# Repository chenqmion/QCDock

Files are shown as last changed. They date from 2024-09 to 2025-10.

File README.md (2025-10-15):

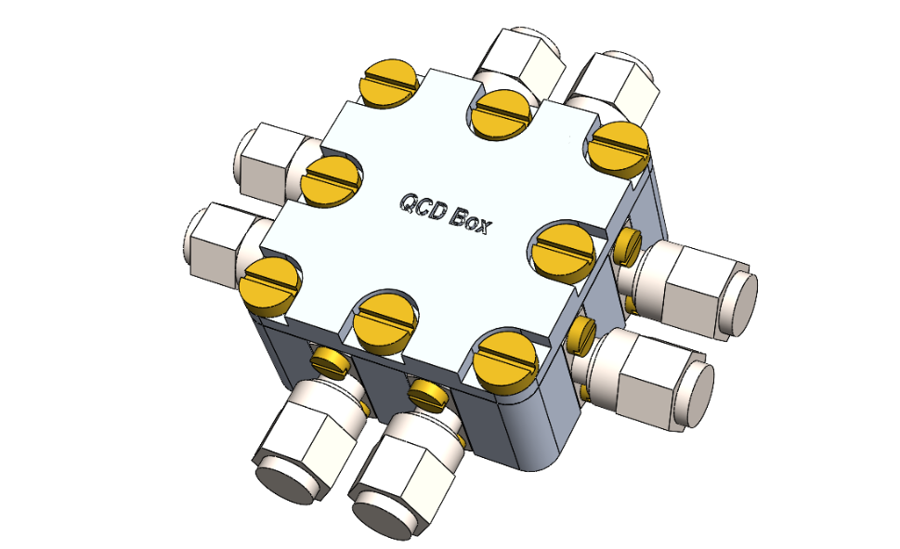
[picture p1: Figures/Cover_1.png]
Preview


# QCDock
This repository contains the **Design** and **Simulation** files of an 8-port sample box developed at QCD Labs. It is designed for 10x10 mm chips. Other chip sizes would require minor modifications of the design files, namely, the PCB and the under-chip cavity. However, chips larger than 13x13mm may encounter wire bonding difficulties.

## Update:
* **20241115** Updated mounting procedure. 
* **20240919** Published V1.0. 

## Description
### Box design in SOLIDWORKS<sup>TM</sup>
* **Box.SLDASM** is the final assembly of the sample box.
* **Bottom.SLDASM** and **Top.SLDASM** are the bottom and top parts, respectively.
* **PCB.SLDASM** is the PCB with GCPW-type transmission lines. <br>
(This file is mainly for consistency check. The actual PCB design files should be found in the **PCB** folder.)
* **SMA.SLDASM** is the SMA connector for consistency check.
* **Chip.SLDASM** is a fake 10x10 mm chip for consistency check.
* **M2_3.SLDASM**, **M2_4.SLDASM**, and **M3_6.SLDASM** are the corresponding screws for consistency check.

\* The **Technical** subfolder contains the .IGS, .SLDDRW, and .pdf files for production.

### PCB design in KiCad<sup>TM</sup>
* **PCB_240916.gds** is the GDSII file designed by a homemade Python<sup>TM</sup> package (pyads).<br>
(pyads is still in the debugging phase and not available to the public at the current time.)
* **gerber** subfolder contains the gerber files.
* The rest of the files are generated by KiCad<sup>TM</sup>.

\* The **.zip** file is for production.

### Box simulation in COMSOL<sup>TM</sup>
* **COMSOL_Eigenmode_Box.mph** simulates the bare box mode.
* **COMSOL_Eigenmode_Full.mph** simulates the box mode with PCB, chip, and wire bonds.<br>
(This file is too large for GitHub. Check out this link to my OneDrive: [COMSOL_Full.mph](https://aaltofi-my.sharepoint.com/:u:/g/personal/qiming_chen_aalto_fi/EXWzsTkU3fFIl8ayYfk28pIBvtJjfRmXe1LOO7rCdNtHGA?e=5WcfCN))

\* The **Geometry** subfolder contains the simplified geometry for simulation.

### PCB simulation in Keysight ADS<sup>TM</sup>
* **QCDBox_wrk.7zads** contains all the simulation files.<br>
(This file is too large for GitHub. Check out this link to my OneDrive: [QCDBox_wrk.7zads](https://aaltofi-my.sharepoint.com/:u:/g/personal/qiming_chen_aalto_fi/EXQFJPZ1qhZAqgtTo-mlQ24B5ay6Y2iGmYVxILdQ2sNBDQ?e=Z6ZQvW))

## Box design 
### Cavity
Bottom (front side)| Bottom (back side)
:---------:|:---------:
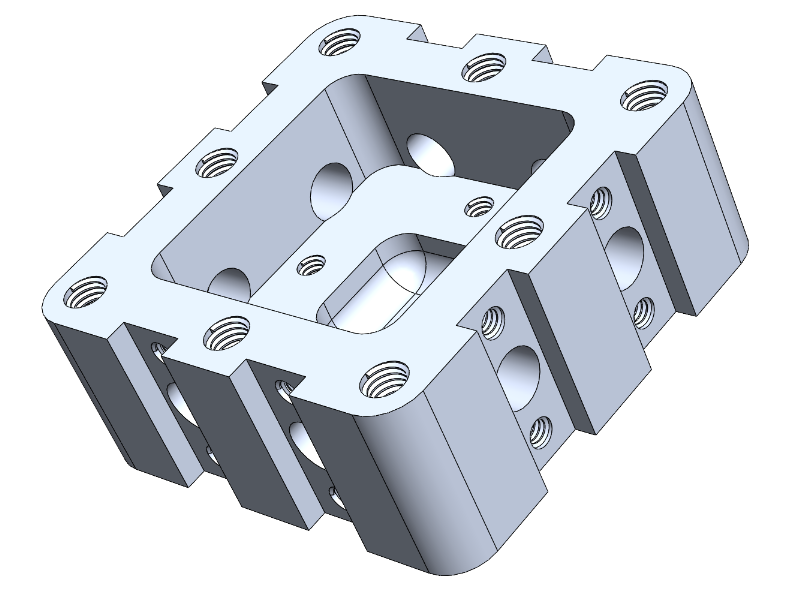
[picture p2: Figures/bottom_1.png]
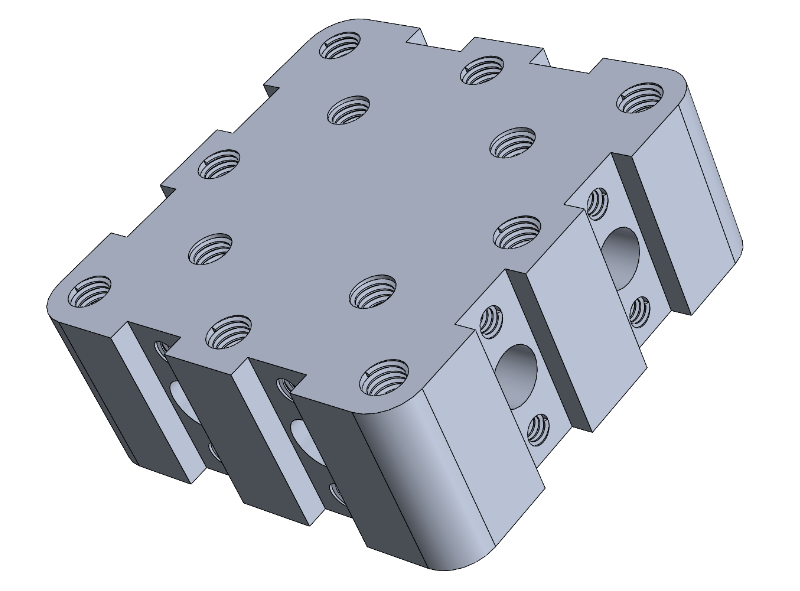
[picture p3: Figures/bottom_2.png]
  |  

Given that the sample box will normally work in the 100MHz -- 8GHz range, we should minimize the box size to push the first box mode as high as possible. The flange size of the SMA connectors (12.9mm) determines the heightness of the box as 13 mm, while its coaxial extention determines the thickness of the side wall as 4 mm. In addition, we add r=3mm fillet for the box.

The inner width of the box is chosen as 21 mm. It will leave a space of 5.5 mm on each side for wire bounding assuming that an 10x10 mm chip is used. This space should be enough considering that the height of the side walls is around 6.5mm. We also add r=2mm fillet for the cavity.

We also designed an empty space below the chip to push the bottom ground further way from the chip. The dimension is 9.5x9.5x3.5 mm in our design, leaving an 0.25 mm distance from the edge to mechanically support the chip. In addition, the chip is supported at the corners by the r=2mm fillet of this under-chip cavity.

Top (front side)| Top (back side)
:---------:|:---------:
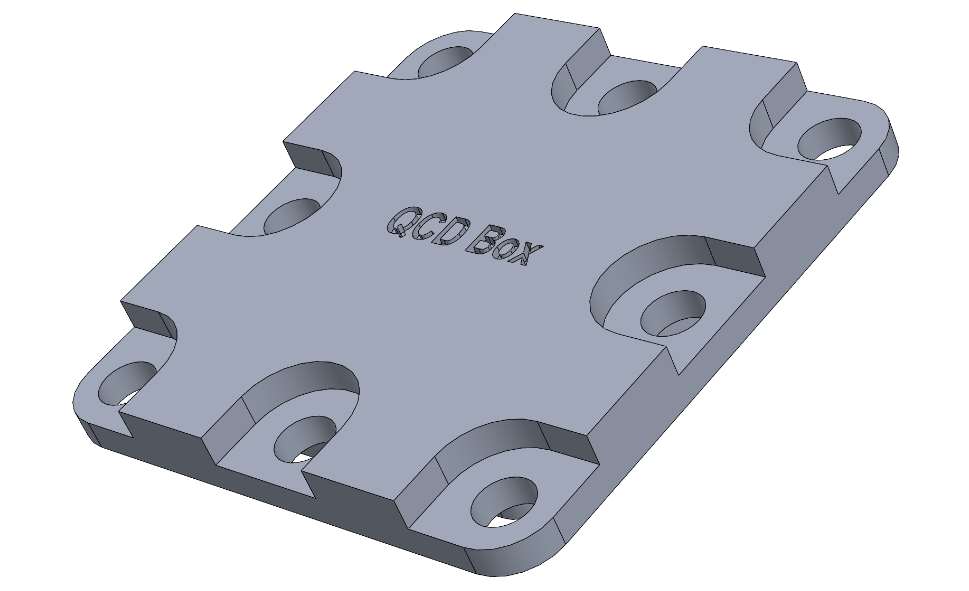
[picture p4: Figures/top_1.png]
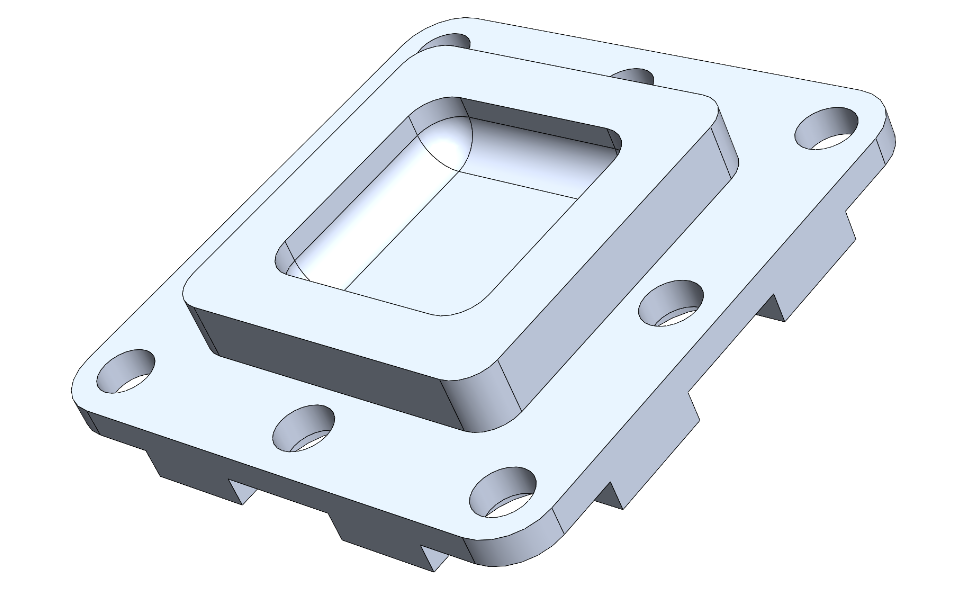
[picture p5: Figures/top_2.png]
  |  

We observe from the simulation that it is useful to have an empty space in the lid to push the first box mode to an even higher frequency. The optimal size of the empty space should be 2/3 of the cavity size, saying 14x14 mm, while the height is not crucial (we choose 3.3 mm). We also add r=2mm fillet for this cavity.

### SMA connectors
To achieve the best impedance match between the SMA connectors and the PCB with minimum efforts, we choose the panel-mount connectors with flat pin. There are only several products of this type available in the market. We choose the M54FM0112F07C model from Micro RF Connector. The extruded pin is 0.8mm-wide and 1.5mm-long, which will determine the launch pad design of the PCB.

The connector has an 0.8mm-diameter 4mm-long impedance-matched extension that can be inserted into the box. They are mounted to the box through 16 M2x4 screws. 

\* The center conductor is gold plated BeCu, which might be slightly magnetic because of Be and the Ni in gold plating process. It may be possible to customize the materials by contacting the company.

### Mounting holes
The box and the lid are assembled with 9 M3x6 screws that are evenly spaced along the edges with an 3mm offset. Owing to the compact size, the threads are designed as through holes that can be used for sample mounting from the back side. 

In addition, we designed 4 addition M3 threads with 3.5mm depth from the back side to faciliate the mounting. A dedicated mounting plate can be used if necessary.

The PCB is mounted inside the cavity via 4 M2x3 screws. Brass may be a good choice of these screws as they provide strength, as well as electrical and thermal condictivities. It will ground the two faces of the PCB to the bulk cavity.

\* Silver paste may be used to improve the electrical and thermal conductivity between the bottom face of PCB and the bulk cavity.

## PCB design 
### GCPW design
We choose ROGERS<sup>TM</sup> 4350B as the PCB material, which has a typical dielectric constant of 3.66. According to ROGERS<sup>TM</sup> online MWI Calculator, the dielectric constant is 3.717 in the "wideband" setting when choosing the thickness as 0.508mm. At specific frequencies, such as 100MHz and 10GHz, it varies from 3.8 to 3.72, respectively. In this design, we choose the dielectric constant at 1GHz as our reference, which is 3.758.

The 0.508mm thickness is chosen for several considerations: The major reason is that a smaller thickness can hardly support the 1mm track width as requested by the SMA connector, assuming that GCPW structure is used. A larger thickness solves this problem, but will lead to a larger geometry that is not very compatible to the chip launcher (a=300um, b=180um). The 0.508mm thickness is a sweet point that fulfils our needs. An additional benefit is that it is comparable to the thickness of our chip (675um).

Impedance (a=1.00 mm, b=0.69 mm)|Impedance 2 (a=0.56 mm, b=0.10 mm)
:---------:|:---------:
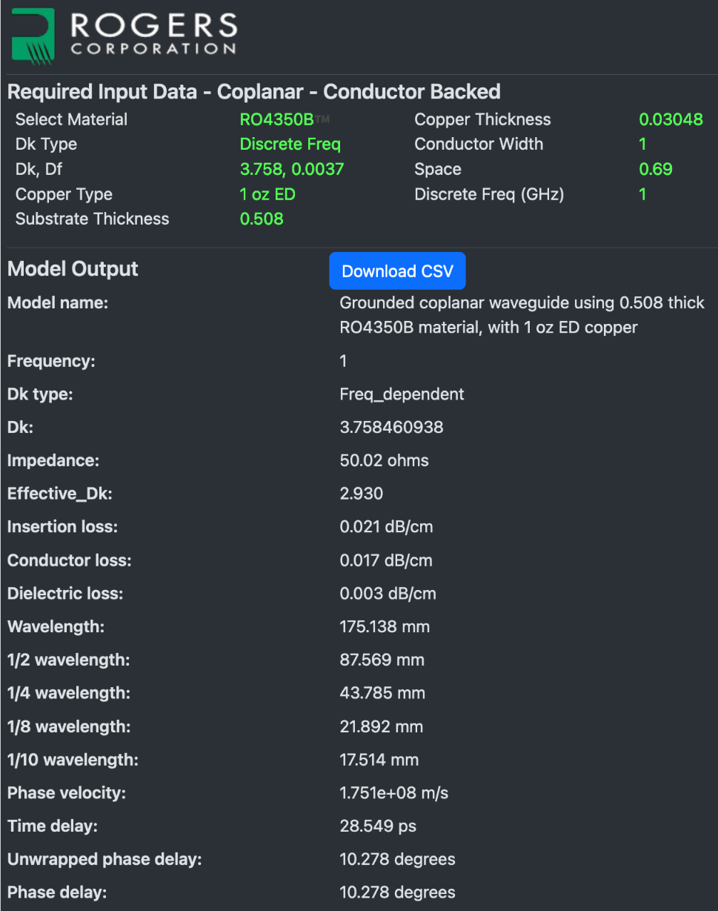
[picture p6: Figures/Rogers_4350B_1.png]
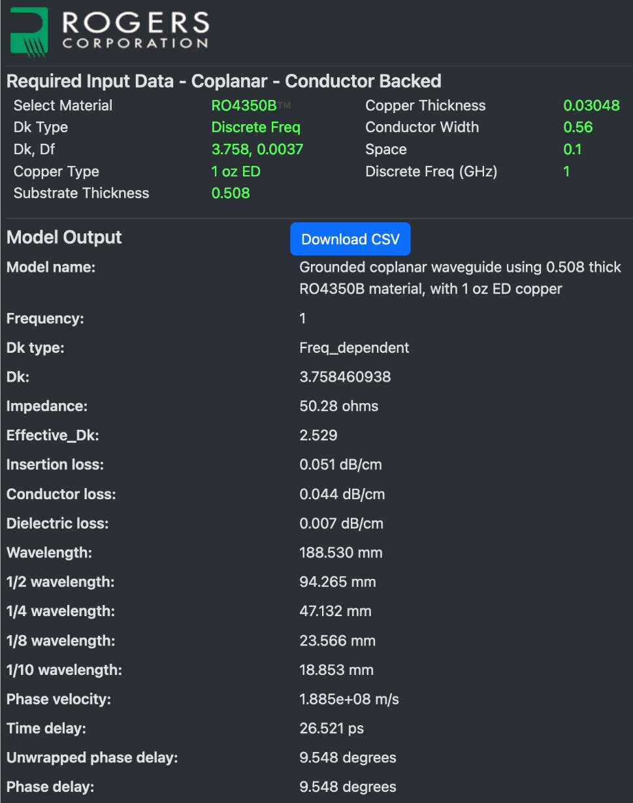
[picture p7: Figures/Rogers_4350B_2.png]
  |  

Using ROGERS<sup>TM</sup> online MWI Calculator, we find two parameter settings that provide good 50Ohm match. Close to the outer side of the PCB, we choose a=1.00mm and b=0.69mm that is convenient for soldering the SMA connectors. We change the design to a=0.56mm and b=0.10mm after 1.5mm from the edge, where an additional 0.65mm taper is designed to connect the two geometries. This 2nd setting is comparable to the on-chip launchers and therefore convenient for wire bonding.

Although a bit skeptical on whether we need vias for such a short waveguide length, the simulation indicates a meaningful improvement of the scattering parameters with them. We choose the via diemeter as 0.2mm. They are 5mm offset from the outer edge of the waveguide slot, and evenly spaced by 8mm alongside the waveguide. In addition, we add vias on the horizontal, vertical, diagonal, and anti-diagonal lines to isolate the 8 waveguides.

PCB (front side)|PCB (back side)
:---------:|:---------:
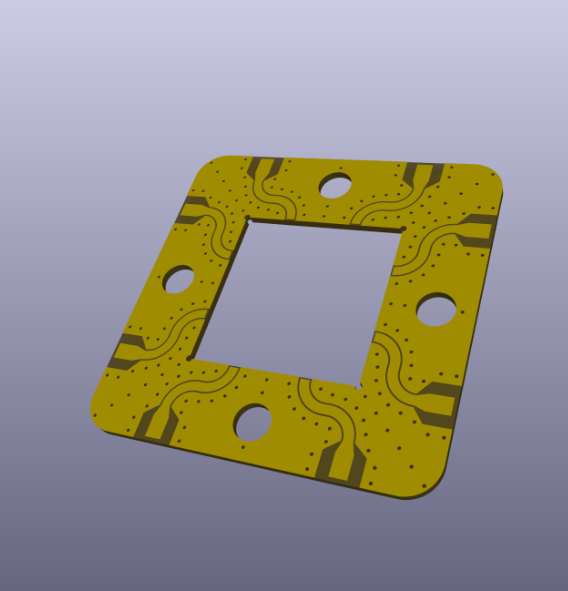
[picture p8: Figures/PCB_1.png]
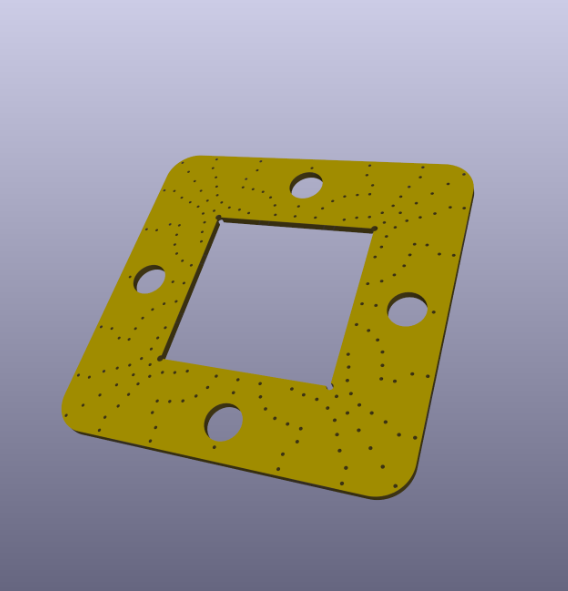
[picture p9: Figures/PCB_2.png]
  |  

The layout is written by a homemade Python<sup>TM</sup> package, pyads. It generates the layout in GDSII format, which can be further converted to gerber files for PCB production (via Keysight ADS<sup>TM</sup>). We find it useful to import the gerber files to KiCad<sup>TM</sup> for a 3D overview. Another benefit is that it can be directly linked to multiple online PCB producers to make the order.

### PCB specification
We choose 2-layer PCB with 1oz copper (35um). The vias are not covered but have 35um-thick copper plating. We choose immersion sliver for surface finish because the standard process of gold plating would require Ni plating beforehand. 

We find in the simulation that the existence of PCB and chip can pull the 1st box mode downwards by multiple gigahertz. This is in some sense unavoidable due to a finite gap between them. However, metalization on the inner edges of the PCB will significantly suppress this effect. We therefore truncate the waveguide 0.1mm from the inner edges and 0.2mm from the outer edges to faciliate edge plating. The 4 screw holes of 2.2mm diameter are also edge plated.

## Box modes
The box-mode simulations are performed by using the Eigenmode solver of COMSOL<sup>TM</sup>. We search for the eigenmodes around 5GHz with normal mesh size. The perfect electric conductor (PEC) condition is applied to the inner surface of the cavity, all the surfaces of PCB, and the upper surface of the chip. In addition, we define 5 wire bonds on each edge of the chip.<br/><br/>

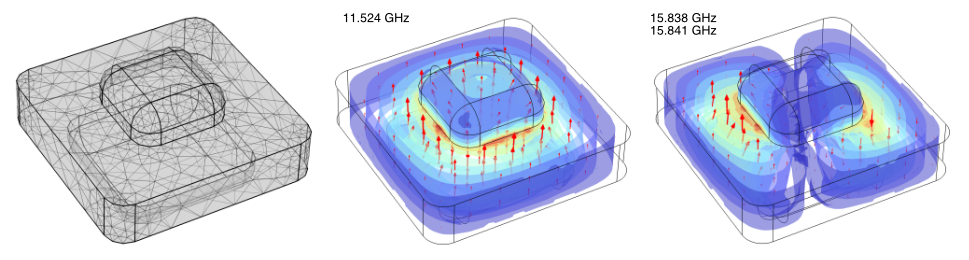
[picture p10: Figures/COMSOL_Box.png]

<em>Fig. 1 Bare box modes. Note that the box is upside down.</em><br/><br/>
We first search for the bare box modes without the PCB and the chip. The first 3 modes are observed at 11.524GHz, 15.838/15.841GHz, and 18.845/18.847GHz, as shown in Fig. 1. This result indicates that the 21mmx21mm cavity size is suitable for operating the box in the 100MHz-8GHz range.<br/><br/>

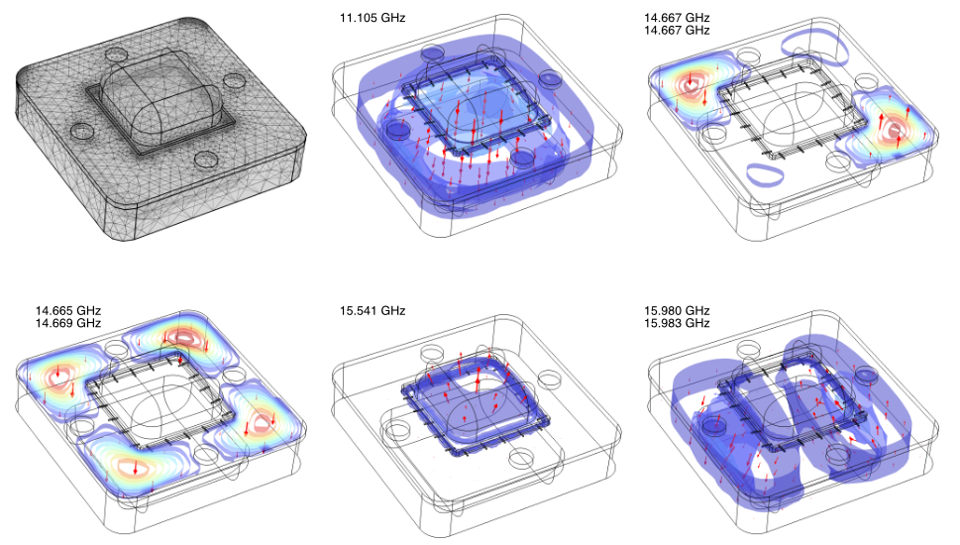
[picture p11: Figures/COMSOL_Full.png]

<em>Fig. 2 Box modes with PCB, chip, and wire bonds. Note that the box is upside down</em><br/><br/>
Next, we add the PCB, chip, and the wire bonds for simulation. The results are summarized in Fig. 2. We find that the 1st are box mode is pulled down to 11.303GHz by introducing the PCB and the chip. The next 4 modes are observed at 11.910/11.912GHz, 14.551GHz, 14.665/14.667/14.669GHz, and 16.226/16.228GHz. Here, the first 2 modes are mostly concentrated to the PCB, the 3rd one is approximately the under-chip cavity mode, while the last one is reminiscent to the 2nd bare box mode.<br/><br/>

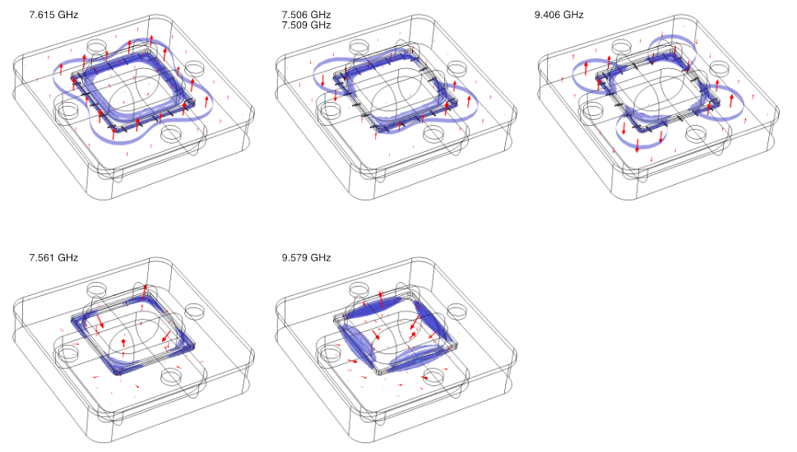
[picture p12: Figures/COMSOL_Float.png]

<em>Fig. 3 Box modes with a floating chip. The upper row has widebonds but not edge plating, while the lower row has edge plating but not wire bonds. Note that the box is upside down</em><br/><br/>
We mentioned before that edge plating of the PCB is important to prevent a substential drop of the 1st box mode in the full simulation. Figure 3 shows the cases with only wire bonds and only edge plating. In both cases, the 1st box mode drops significantly to approximately 7.5GHz. However, the field profiles suggest different mechanisms for the drop: The mode spreads over the PCB in the former case, while it is mostly concentrated in the gap between PCB and the chip in the latter case. This observation reveals the importance of PCB edge plating. Fortunately, it is a standard technique in the PCB inductry.

## PCB characteristics
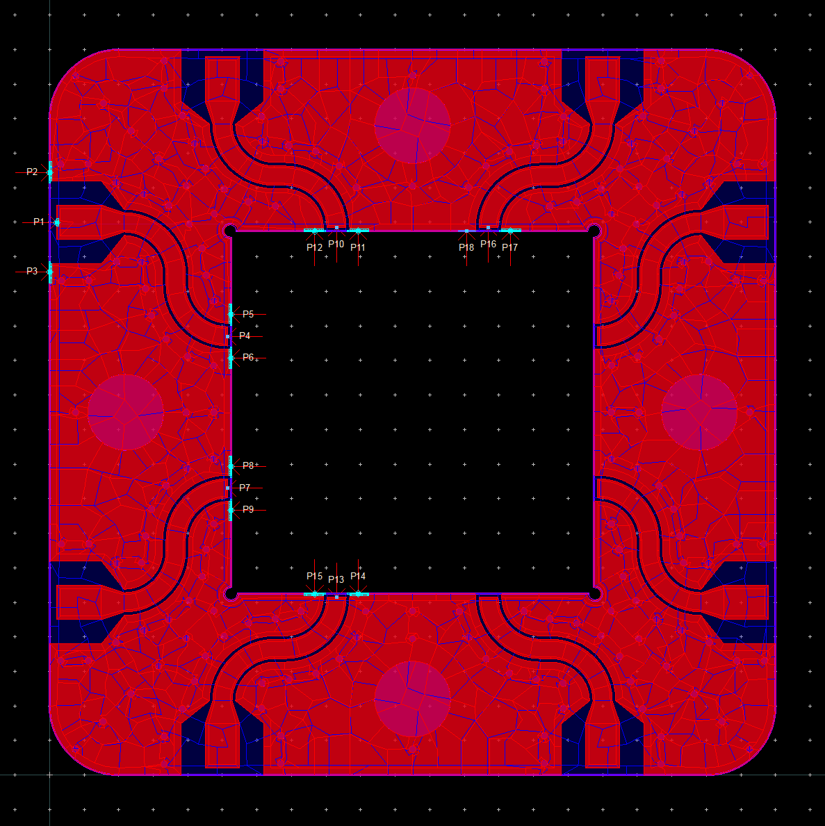
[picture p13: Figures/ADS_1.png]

<em>Fig. 4 Mesh and port definition for PCB simulation.</em><br/><br/>
The PCB simulations are performed by using the Momentum solver of Keysight ADS<sup>TM</sup>. We define the WN port as the inout port, while the rest as output ports. The pin edge size connected to the center conductor is 0.1mm, while it is 0.5mm when connected to the top-face ground.

We simulate the scattering coefficients of the WN waveguide, as well as its crosstalk to the nearest and next nearest waveguides. We perform the adaptive frequency sweep from DC to 10GHz with maximamly 51 points. The mesh is defined at the highest simulation frequency with a density of 20 per wavelength. The automatic edge mesh is enabled and mesh reduction allowed.

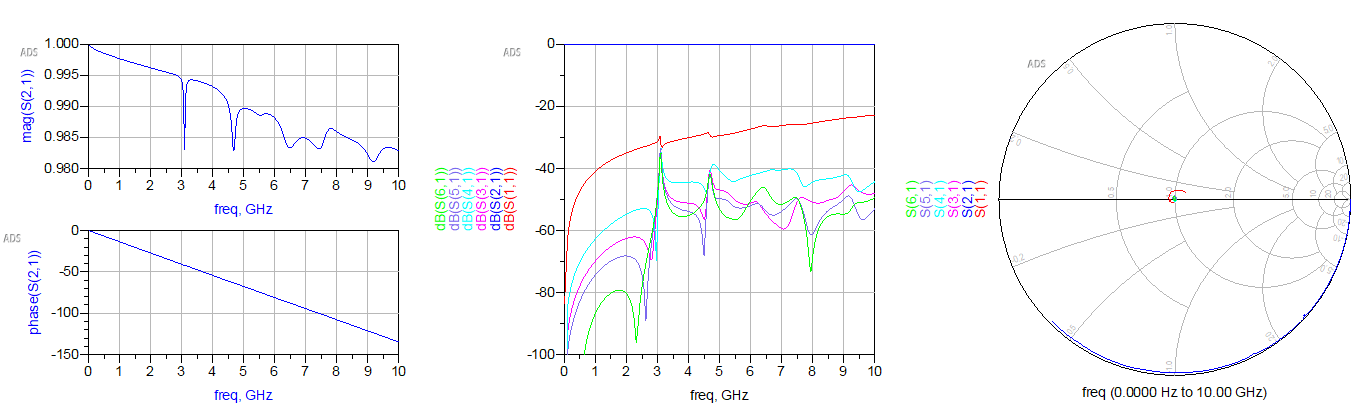
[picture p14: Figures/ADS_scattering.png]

<em>Fig. 5 Scattering parameters.</em><br/><br/>
Figure 5 summarizes the simulation results. The transmission and reflection rates of a single waveguide are -0.18dB and -22dB in the worst case, respectively. It indicates a good 50OHm impedance match, as can be also seen from the Smith chart. Moreover, the crosstalk between nearest and next nearest waveguides are approximately -50dB.<br/><br/>

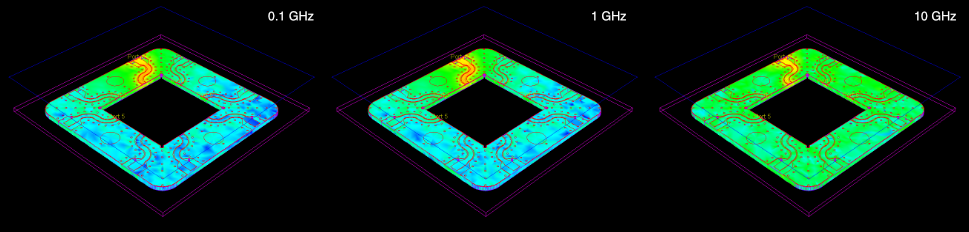
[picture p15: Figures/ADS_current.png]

<em>Fig. 6 Current density in dB scale.</em><br/><br/>
We observe impedance mismatches at 3, 4.7, 6.5GHz in the scattering coefficients. However, the current density profile does not show obvious difference at these frequencies. We note that this mismatch perturbes the transmission rate by less than 1%, although it may look huge in the dB scale. 

## Mounting procedure:
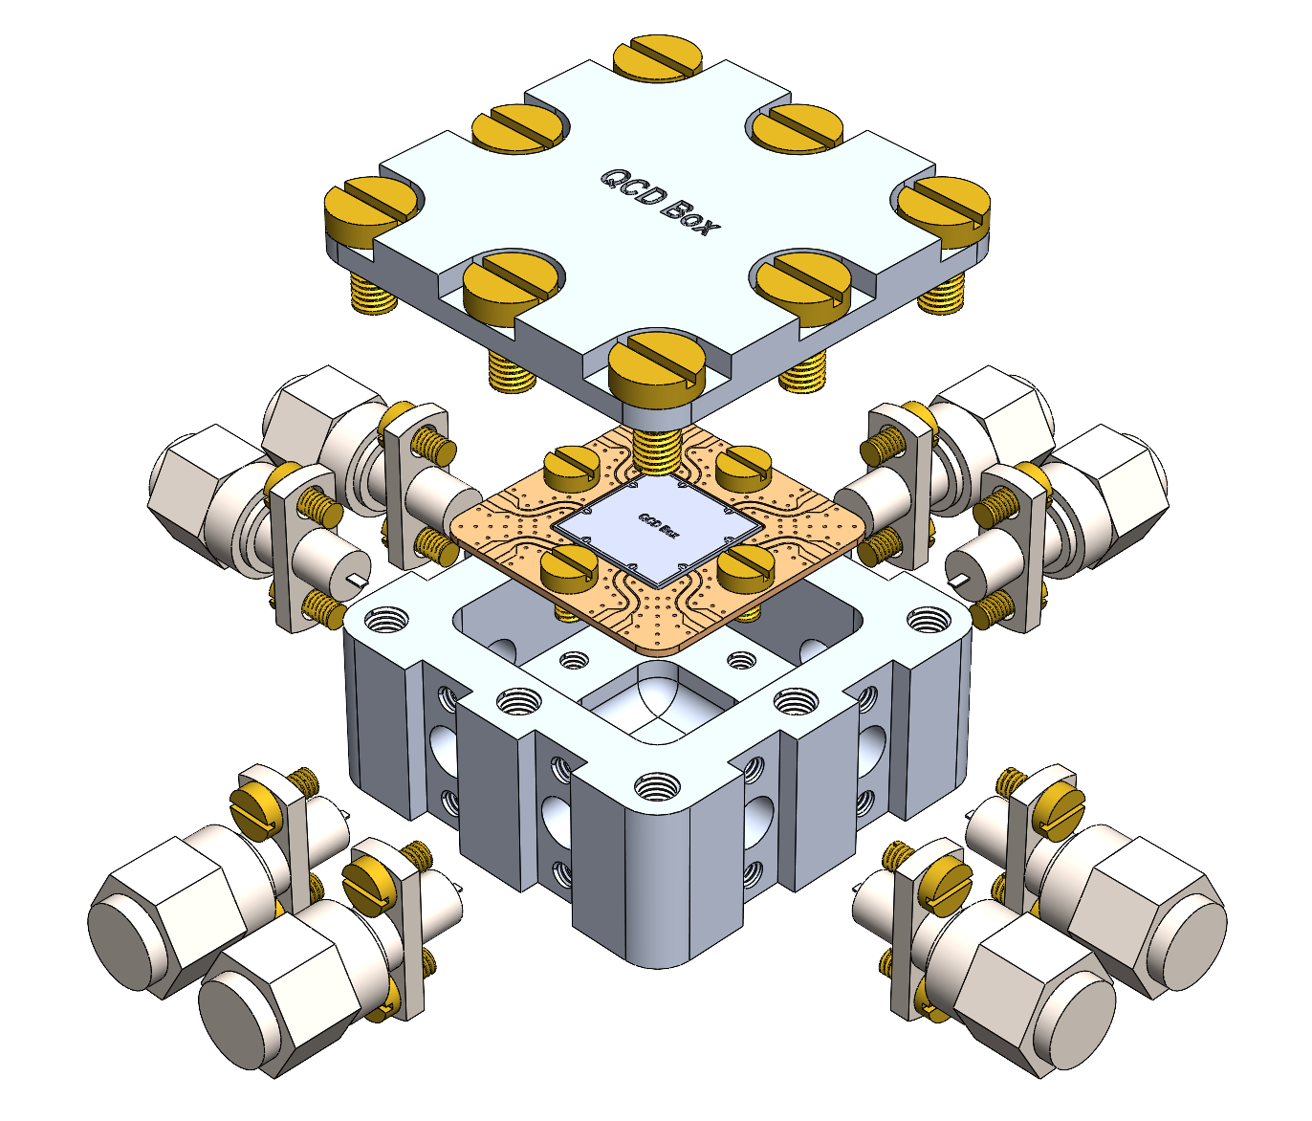
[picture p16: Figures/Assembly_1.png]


Place PCB inside the cavity, align it to the center, and mount it with the 4 M2x3 screws (This will prevent pulling up the PCB during soldering, which is originated from the surface tension of the solder when melting).

Spread a very small amount of solder paste onto the waveguide tracks, then onto the tips of SMA connectors.

Insert the SMA connectors into the holes on the side wall and tighten them with M2x4 screws. 

Check if the solder paste have a good contact between the SMA tip and the waveguide track. Use needle to add more solder paste if necessary.

Use heat gun to melt the solder paste (Use its highest power). The solder paste starts floating in ~30s, and start turning into a shining color in ~1min. 

Wait for ~10s more so that all the soldering areas looks shining and smooth. 

Turn off the heat gun and use twizer to transfer the box into a cold metal plate (The box is very hot right now).

Wait ~5min for cool down, then use multimeter to check DC connection between the SMA pin and the waveguide.

## Acknowledgement:
We are delighted if you find this project helpful to your own study. Feel free to contact us if you have questions, suggestions, criticisms, etc. You are free to copy, share, and build on this project without notifying the authors.

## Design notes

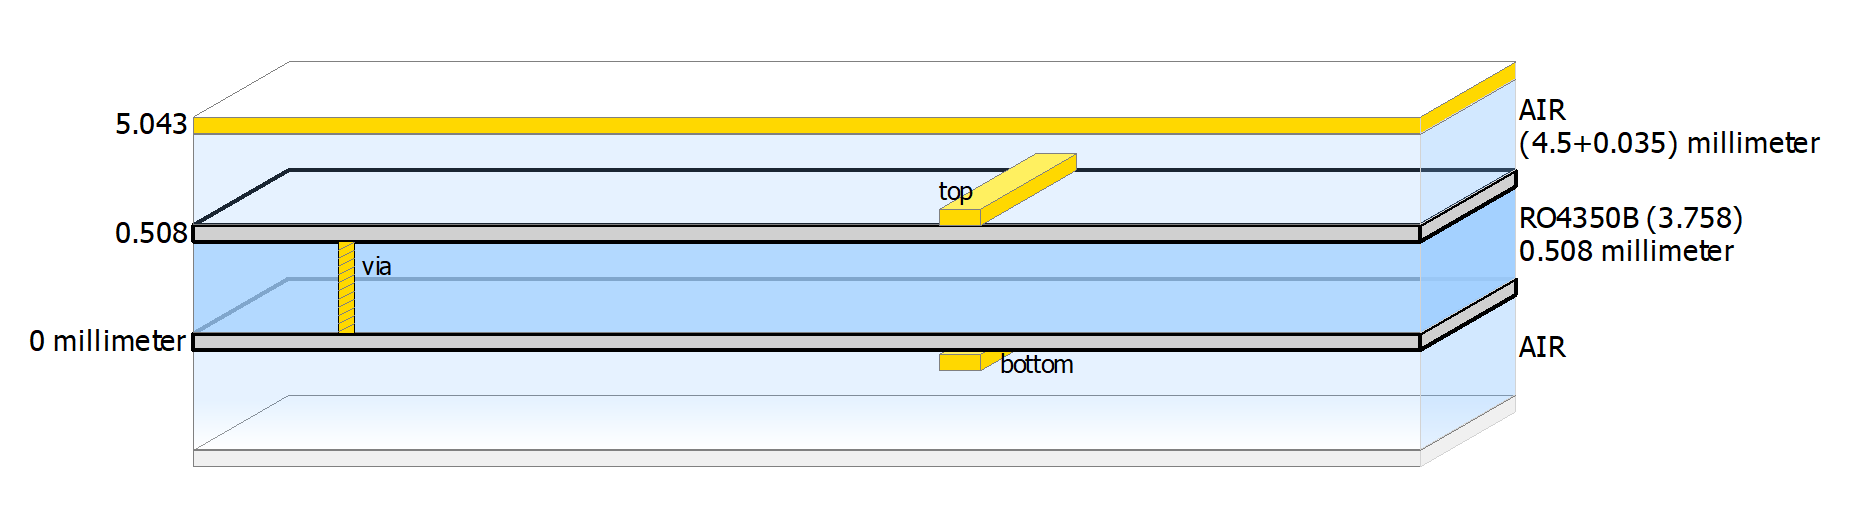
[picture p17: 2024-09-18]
Figures/ADS_2.png

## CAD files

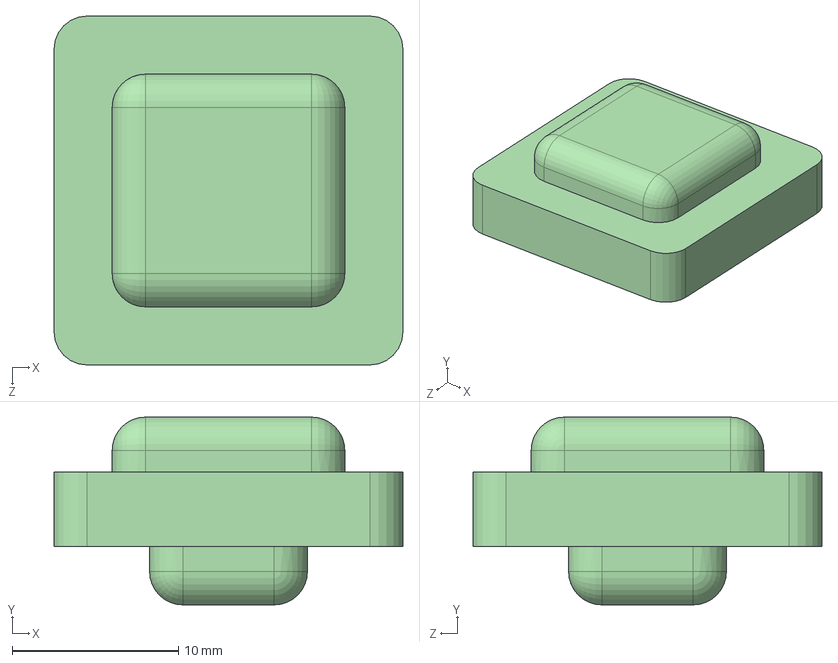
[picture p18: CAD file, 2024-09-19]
COMSOL/Geometry/COMSOL_QCDBox.SLDASM
21.0 x 11.3 x 21.0 mm
COMSOL_Box
COMSOL_PCB
COMSOL_Chip
COMSOL_Bond x 2

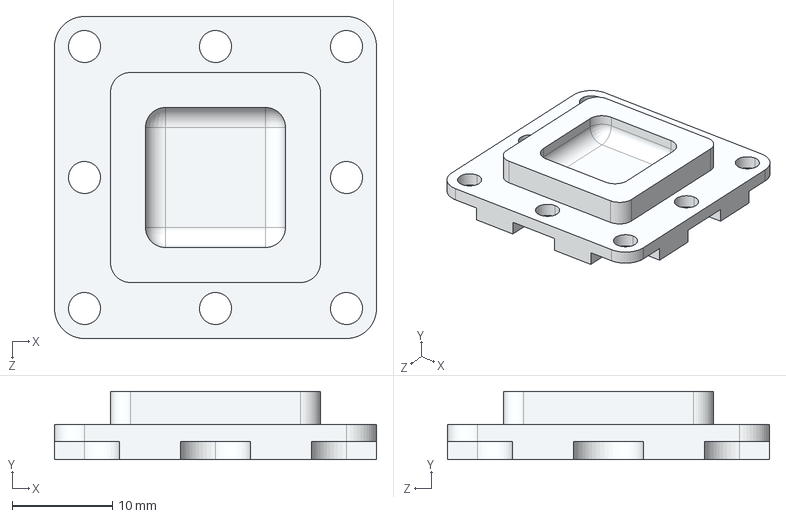
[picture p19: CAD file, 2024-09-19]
Box/Technical/top.IGS
32.2 x 6.80 x 32.2 mm

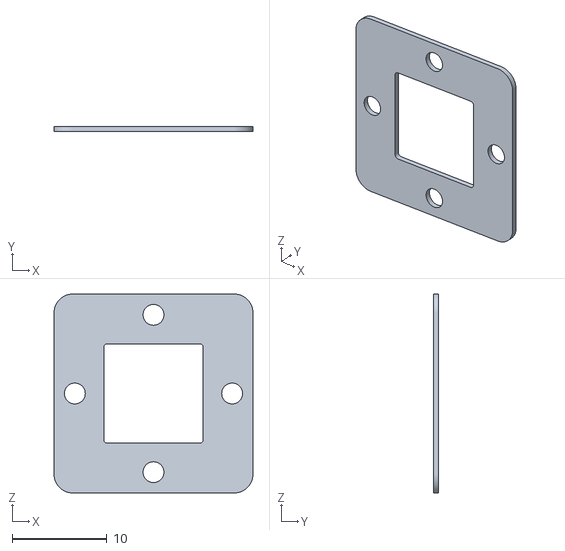
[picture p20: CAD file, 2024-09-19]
COMSOL/Geometry/COMSOL_QCDBox - COMSOL_PCB-1.STL
21.0 x 0.58 x 21.0

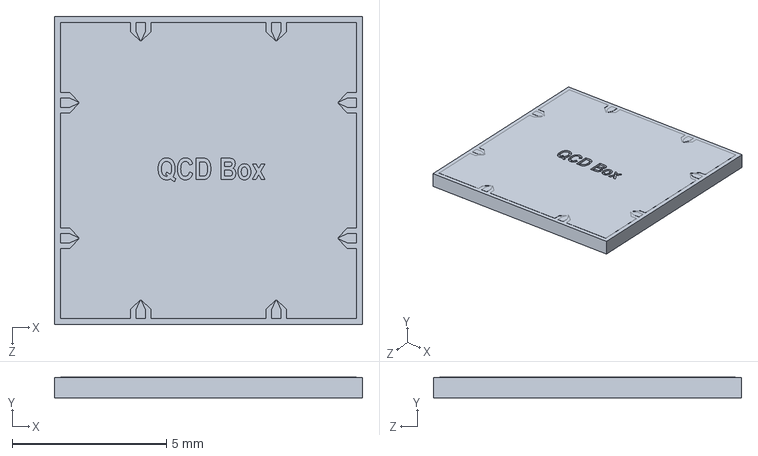
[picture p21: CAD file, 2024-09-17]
Box/chip.SLDPRT
10.0 x 0.675 x 10.0 mm

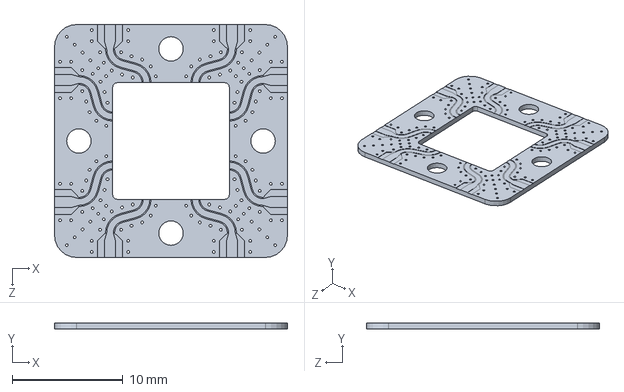
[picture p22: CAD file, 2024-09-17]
Box/PCB.SLDPRT
21.0 x 0.58 x 21.0 mm

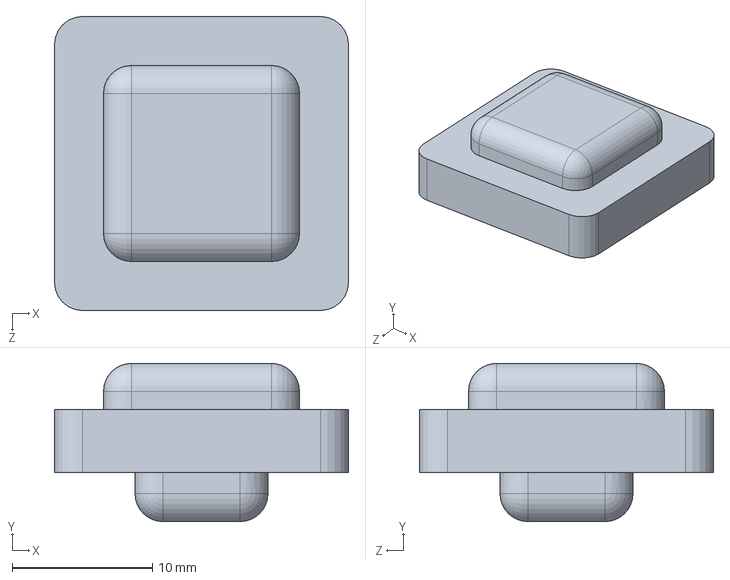
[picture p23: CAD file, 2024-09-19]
COMSOL/Geometry/COMSOL_Box.SLDPRT
21.0 x 11.3 x 21.0 mm

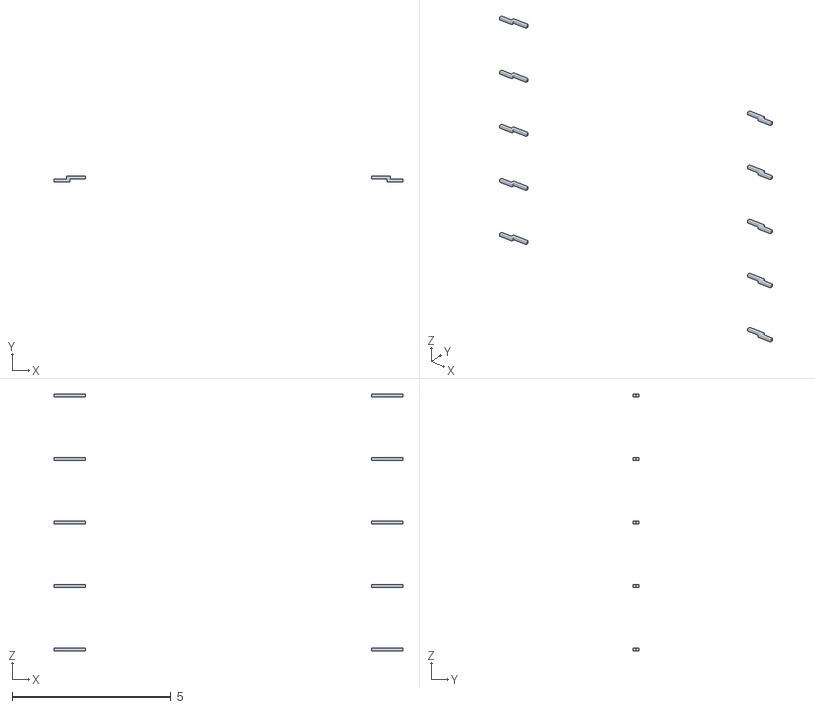
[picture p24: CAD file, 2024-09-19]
COMSOL/Geometry/COMSOL_QCDBox - COMSOL_Bond-1.STL
11.0 x 0.2 x 8.10

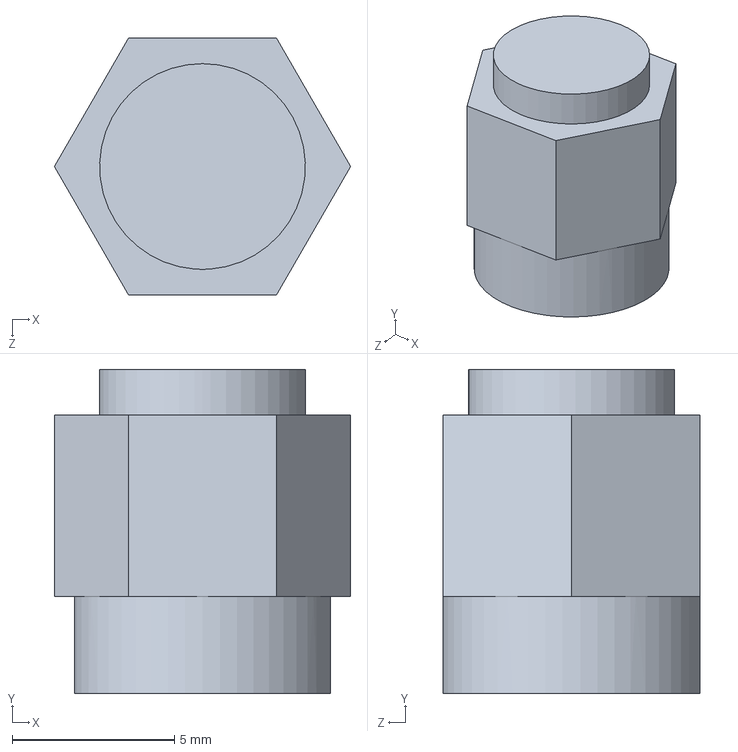
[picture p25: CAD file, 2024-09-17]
Box/SMA_short.SLDPRT
9.15 x 10.0 x 7.92 mm

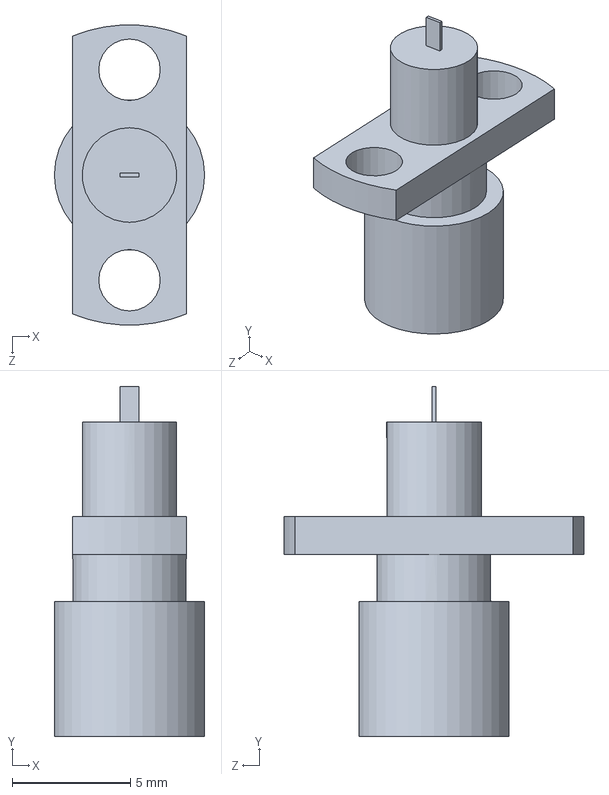
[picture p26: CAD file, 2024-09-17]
Box/SMA.SLDPRT
6.35 x 14.8 x 12.7 mm

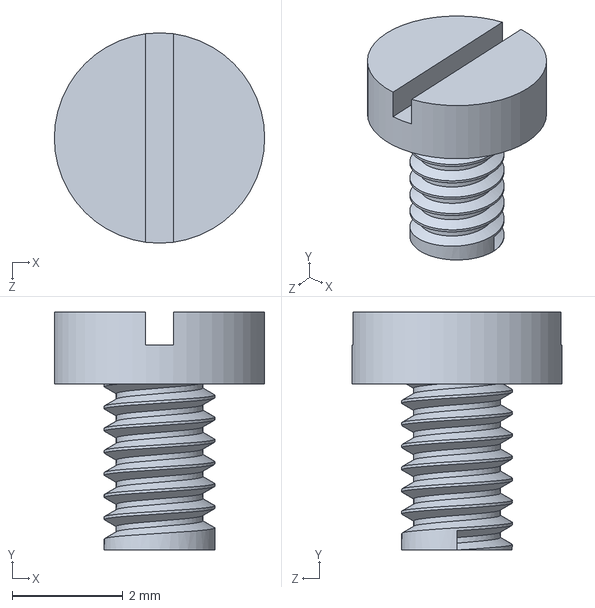
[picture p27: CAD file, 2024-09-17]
Box/M2_3mm.SLDPRT
3.80 x 4.30 x 3.80 mm

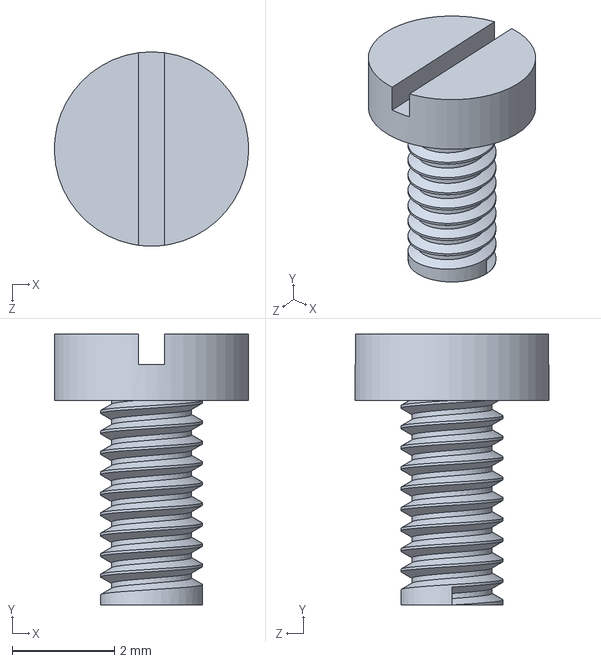
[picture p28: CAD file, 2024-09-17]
Box/M2_4mm.SLDPRT
3.80 x 5.30 x 3.80 mm

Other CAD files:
COMSOL/Geometry/COMSOL_QCDBox - COMSOL_Chip-1.STL
COMSOL/Geometry/COMSOL_QCDBox - COMSOL_Bond-2.STL
Box/top.SLDPRT
COMSOL/Geometry/COMSOL_QCDBox - COMSOL_Box-1.STL
COMSOL/Geometry/COMSOL_PCB.SLDPRT
COMSOL/Geometry/COMSOL_Chip.SLDPRT
COMSOL/Geometry/COMSOL_Bond.SLDPRT
Box/M3_6mm.SLDPRT
Box/Technical/top.SLDDRW

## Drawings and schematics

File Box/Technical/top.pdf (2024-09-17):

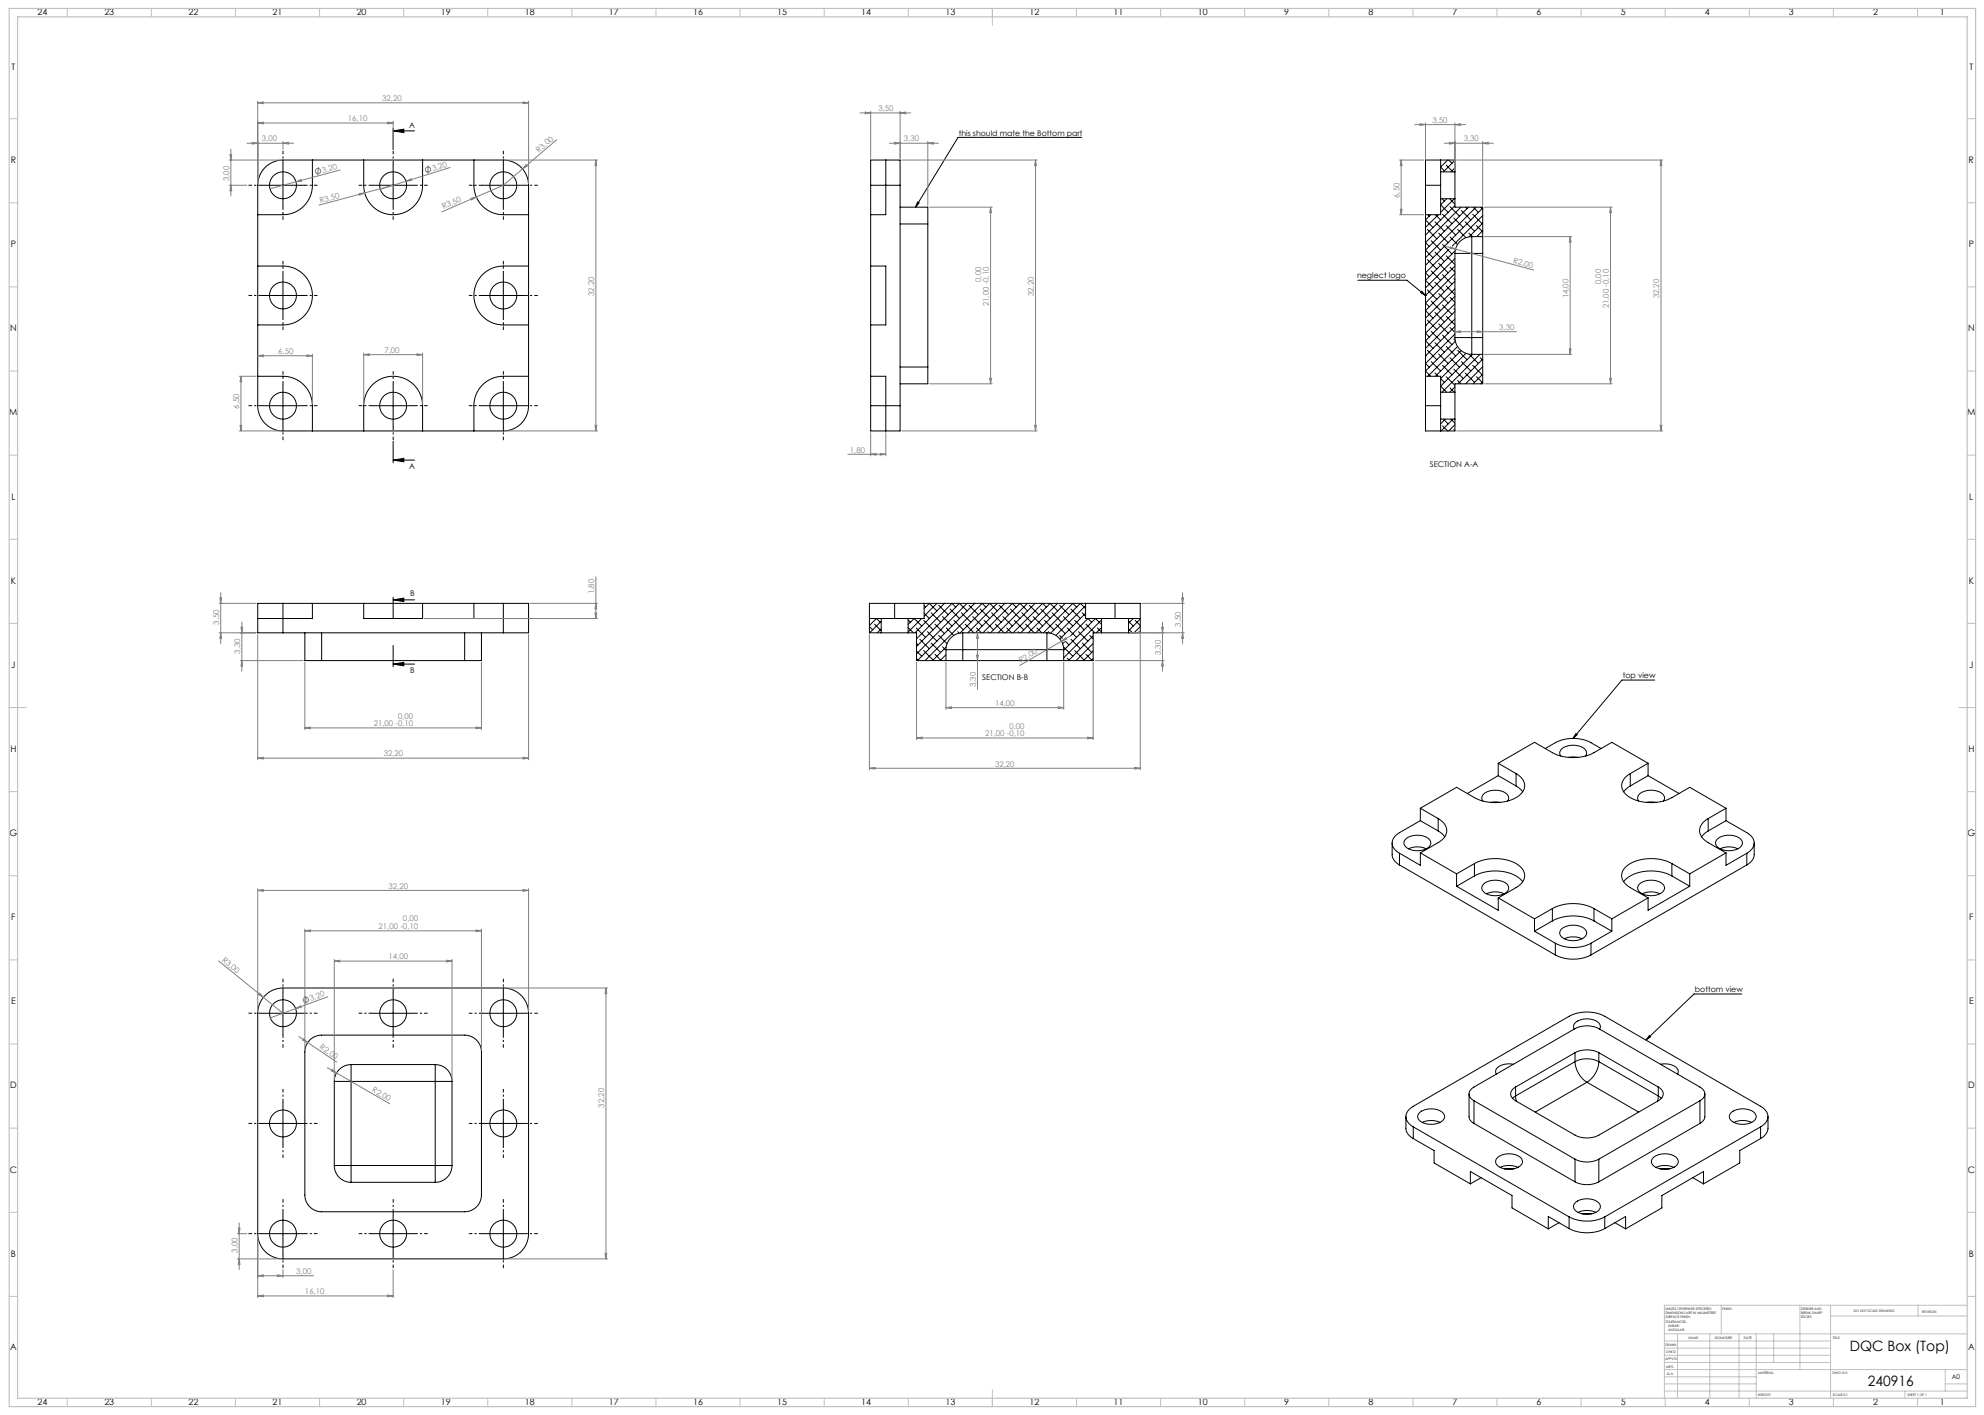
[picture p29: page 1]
top view; bottom view; SECTION A-A; neglect logo; SECTION B-B; FINISH:; DEBURR AND; BREAK SHARP; DO NOT SCALE DRAWING; REVISION; SCALE:5:1; SHEET 1 OF 1; DQC Box (Top)

this should mate the Bottom part

UNLESS OTHERWISE SPECIFIED:
DIMENSIONS ARE IN MILLIMETERS
SURFACE FINISH:
TOLERANCES:
LINEAR:
ANGULAR:

NAME | SIGNATURE | DATE | | | | TITLE:

DRAWN
CHK'D
APPV'D
MFG
Q.A | | | | MATERIAL: | DWG NO. 240916 | A0

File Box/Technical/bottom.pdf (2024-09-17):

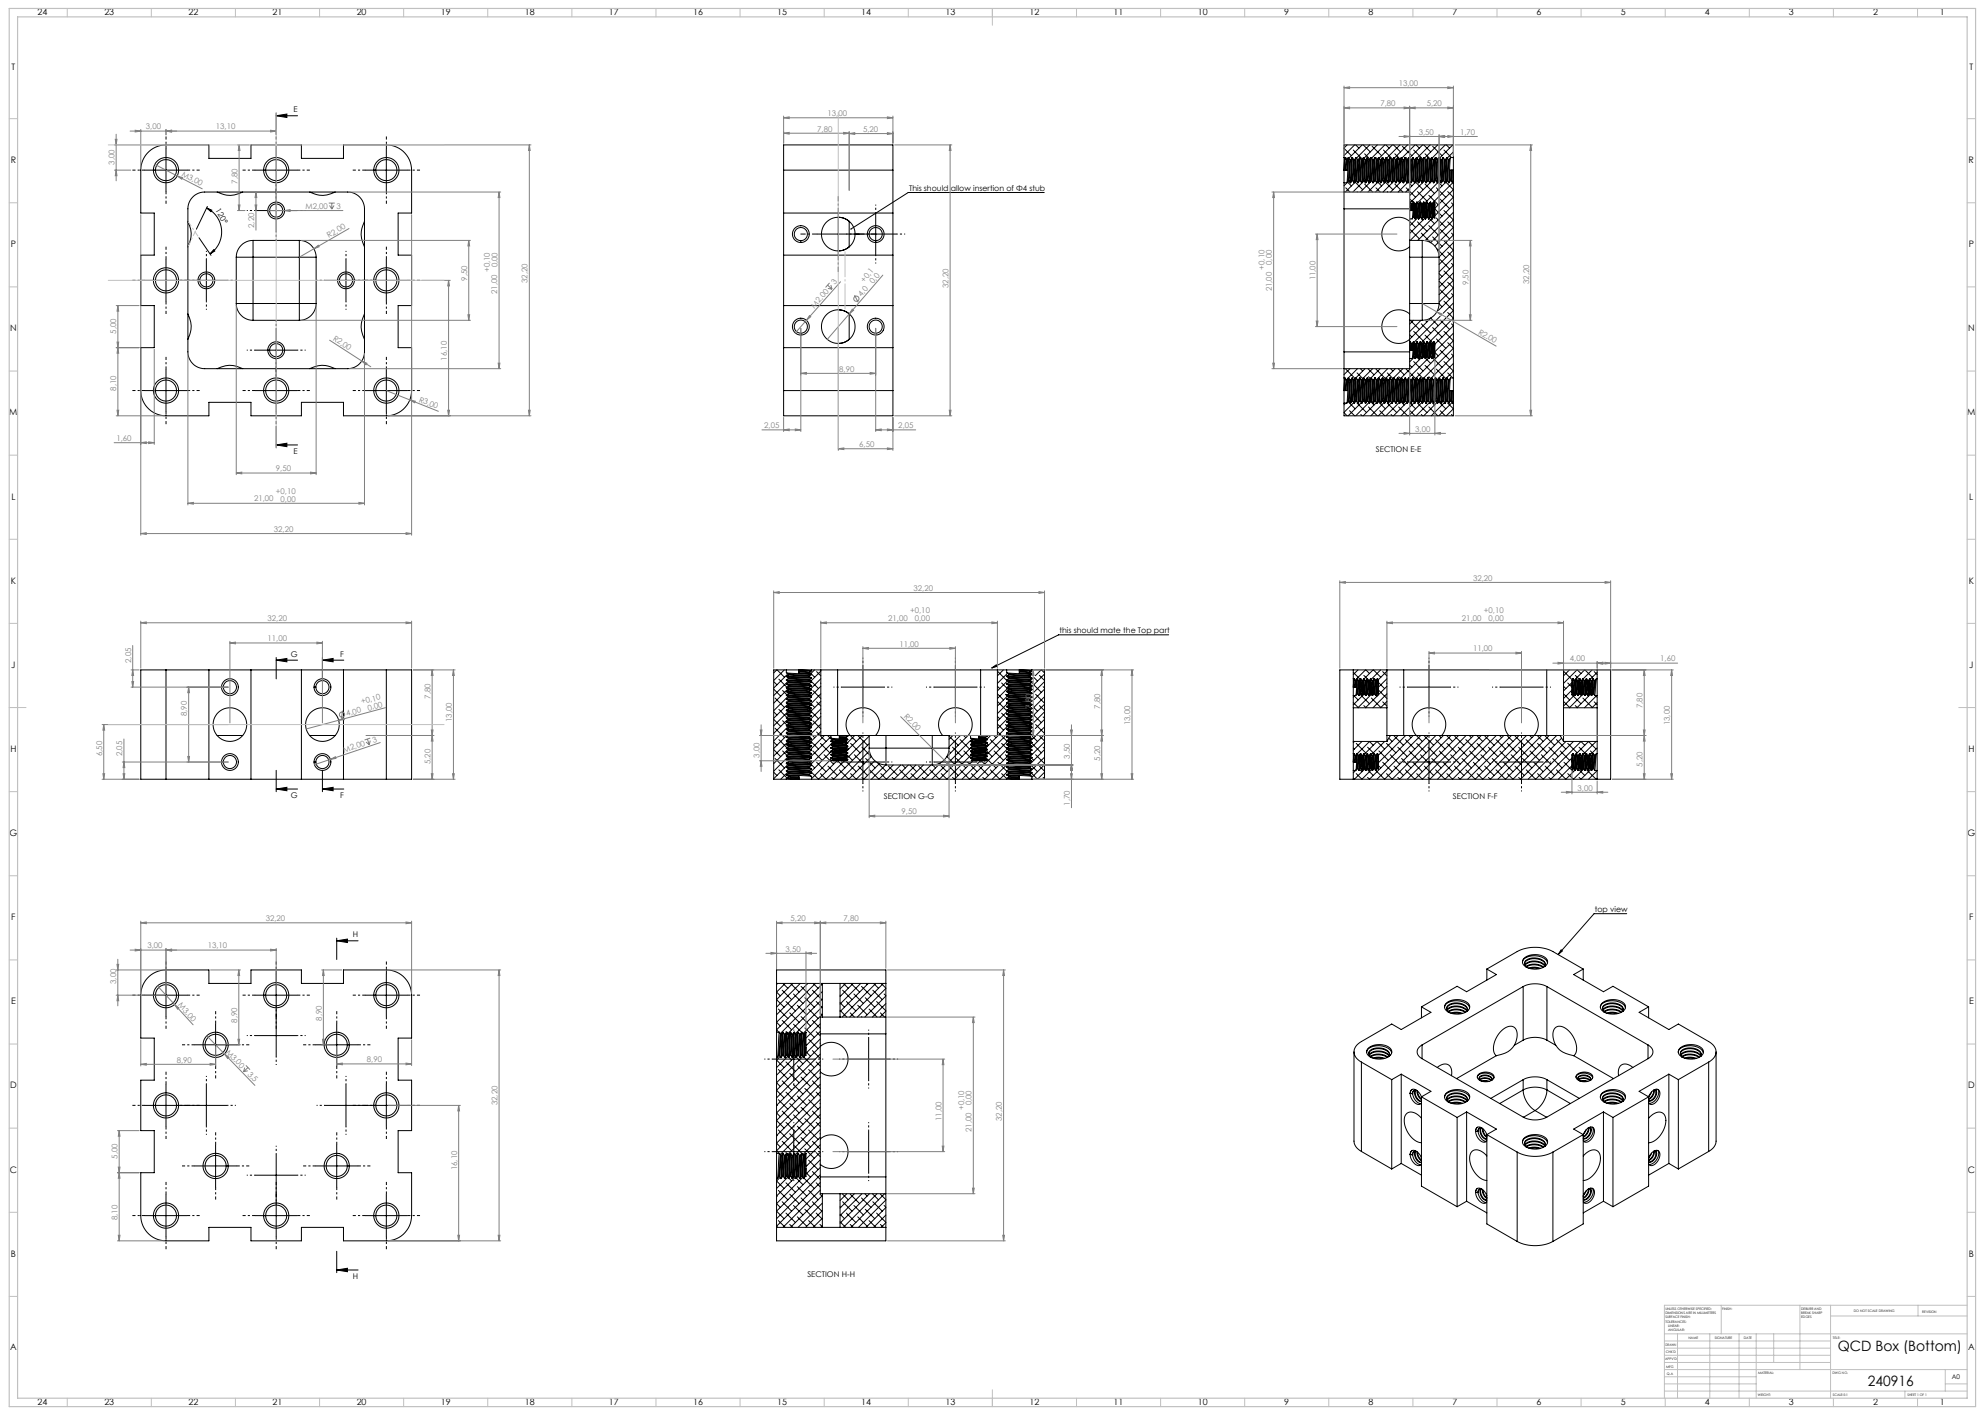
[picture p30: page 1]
SECTION E-E; SECTION F-F; SECTION G-G; SECTION H-H; top view; FINISH:; DEBURR AND; BREAK SHARP; DO NOT SCALE DRAWING; REVISION; SCALE:5:1; SHEET 1 OF 1; QCD Box (Bottom)

This should allow insertion of Φ4 stub

this should mate the Top part

UNLESS OTHERWISE SPECIFIED:
DIMENSIONS ARE IN MILLIMETERS
SURFACE FINISH:
TOLERANCES:
LINEAR:
ANGULAR:

NAME | SIGNATURE | DATE | | | | TITLE:

DRAWN
CHK'D
APPV'D
MFG
Q.A | | | | MATERIAL: | DWG NO. 240916 | A0

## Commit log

2024-09-17 Update and rename QCD_Box_1.kicad_pcb to PCB/QCD_Box_1.kicad_pcb
    [QCD_Box_1.kicad_pcb]
2024-09-17 Update and rename PCB/boardBound.gbr to PCB/gerber/boardBound.gbr
    [boardBound.gbr]
